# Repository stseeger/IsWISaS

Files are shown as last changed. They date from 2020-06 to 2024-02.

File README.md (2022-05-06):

# IsWISaS
(I)n-(s)itu (W)ater (I)sotope (Sa)mpling (S)ystem

This repository contains Hardware (circuit board designs), the respective Firmware and Software (a collection of scripts) that enable the user to control a set of electric solenoid valves and up to two mass flow controllers.

In conjunction with some in-situ gas sampling probes and a cavity ring down spectrometer (CRDS), this should facilitate fully automated long term in-situ measurements of stable water isotopes.

In case you need something that works, please contact me under: stefan.seeger@hydrology.uni-freiburg.de
There are working setups, but the Hardware is completely undocumented (most of my time is spent on getting results, not writing documentations) and the Software is constantly changing.

Right now everything in this repository is still work in progress. A technical note is planned...

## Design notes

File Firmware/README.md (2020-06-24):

Each of the different controller types should respond to the same set of serial text commands:  
  
**?**: return device class, devce type and version (seperated by spaces)  
**valve**: return the active valve  
**valve #**: activate valve # and close previous active valve  
**flow**: return the analog voltages (in mV) returned by the two mass flow controllers (seperated by spaces)  
**flow a b**: change the set point voltages of the two flow controllers (A and B) to a and b (in mV)

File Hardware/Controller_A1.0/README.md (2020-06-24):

This circuit board is meant to control up to two mass flow controllers and up to 16 solenoid valves.  
  
Part list:  
1 x Arduino Nano v3  
2 x ULN2803  
2 x 1kOhm Resitor  
2 x 100kOhm Resistor  
2 x 100µF Capacitator  
2 x PS/2 Port  
2 x 10 slot female header

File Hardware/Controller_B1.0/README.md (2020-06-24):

The main circuit board is meant to control up to two mass flow controllers and up to 8 solenoid valves.

Each extension circuit board can control up to 8 additional solenoid valves. The main board has one RJ-45 port that can be used to connect to the first extension and each extension has two RJ-45 ports (in and out), so that multiple extensions can be chained together.

The main board has a RJ-45 port which can be used to connect to an extension board which itself can control up to 8 solenoid valves.
  
Part list (main circuit board):  
1 x Arduino Nano v3  
1 x ULN2803  
2 x 1kOhm Resitor  
2 x 100kOhm Resistor  
2 x 100µF Capacitator  
2 x PS/2 Port  
1 x 8 slot female header  
1 x RJ-45 Port  
  
Part list (extension board):  
1 x 74HC595  
1 x ULN2803  
1 x 8 slot female header  
2 x RJ-45 Port

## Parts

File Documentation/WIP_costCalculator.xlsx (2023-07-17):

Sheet: fullSetup
# of setups | 1
# of WIPs | 76 | average tubing length [m] | 3
# of boxes | 10
part | EUR/piece | 1/WIP_or_setup | cost/WIP_or_setup | total amount | total cost | part # | url
MFC | 1207 | 2 | 2414 | 2 | 2414 | 35362L | https://analyt-mtc.de/de/contact-2
valve | 30 | 3 | 90 | 228 | 6840 | E210C-2W012 | https://shop.clippard.eu/en/product=e210c-2w012&id=evmmnc343t
valve block | 65.5 | 0.375 | 24.5625 | 28.5 | 1866.75 |  | http://www.schneider-fertigungstechnik.de/
mixing chamber | 21.36 | 1 | 21.36 | 76 | 1623.36 |  | https://kunststoffverarbeitung-freiburg.de/
probe head | 28.6 | 1 | 28.6 | 76 | 2173.6 |  | https://www.porex.com/
1/16" fitting bla | 3.93 | 1 | 3.93 | 76 | 298.68 | UP XP-201X | https://techlab.de/web/index.php?WSparam=2&WSdaten=5842@0
1/16" fitting red | 3.93 | 1 | 3.93 | 76 | 298.68 | UP XP-202X | https://techlab.de/web/index.php?WSparam=2&WSdaten=5844@0
1/16" nut blue | 2.26 | 1 | 2.26 | 76 | 171.76 | UP P-206 | https://techlab.de/web/index.php?WSparam=2&WSdaten=1989@0
ferrule | 2.16 | 1 | 2.16 | 76 | 164.16 | UP P-200X | https://techlab.de/web/index.php?WSparam=2&WSdaten=1978@0
1/8" fitting bla | 3.93 |  |  | 60 | 235.8 | UP XP-301X | https://techlab.de/web/index.php?WSparam=2&WSdaten=5878@0
1/16" FEP | 2.86 | 9 | 25.74 | 684 | 1956.24 | KAP 100.968 | https://techlab.de/web/index.php?WSparam=2&WSdaten=4537@0
9 mm PVC | 0.45 | 3 | 1.35 | 228 | 102.6 | PVC 69 | https://www.landefeld.de/artikel/de/pvc-schlauch-6x9mm-transparent-meterware/PVC%2069
 |  |  |  |  | 18145.63

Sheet: WIP
Setup characteristics
distance probe to valve manifold [m]: | 3 |  | Legend:
distance manifold to analyzer [m]: | 38.9 |  | fix input
probes per valve manifold: | 9.3 |  | variable input
number of lines per probe: | 3 |  | computed values
total number of probes: | 76
IsWIP cost calculation
Part | per probe | cost per piece [EUR] | cost per probe [EUR] | total cost [EUR] | pieces in stock | credit [EUR] | missing pieces | remaining cost [EUR]
mixing chamber | 1 | 15 | 17.85 | 1140.00 | 150 | 1140.00 | 0 | 0.00
probe head | 1 | 34 | 34.00 | 2584.00 | 150 | 2584.00 | 0 | 0.00
Flangeless nut+ferrule | 3 | 3.81 | 11.43 | 868.68 | 30 | 114.30 | 198 | 754.38
Aluminium pipe (10x3mm) | 0.1 | 10.4 | 1.04 | 79.04 | 1 | 10.40 | 7 | 72.80
PAFL-tubing (12x9mm) at shaft | 0.1 | 5.47 | 0.55 | 41.57 | 0 | 0.00 | 8 | 43.76
outer PVC-tubing (9x6mm) | 7.182795699 | 0.71 | 5.10 | 387.58 | 0 | 0.00 | 546 | 387.66
1/16” FEP-tubing | 9 | 2.86 | 25.74 | 1956.24 | 250 | 715.00 | 434 | 1241.24
1/8" FEP-tubing | 12.5483871 | 1.4 | 17.57 | 1335.15 | 0 | 0.00 | 954 | 1335.60
solenoid valve | 3 | 30 | 90.00 | 6840.00 | 48 | 1440.00 | 180 | 5400.00
valve manifold | 0.3225806452 | 65 | 20.97 | 1593.55 | 6 | 390.00 | 19 | 1235.00
complete probe |  |  | 224.24 | 16825.81 |  | 6393.70 |  | 10470.44

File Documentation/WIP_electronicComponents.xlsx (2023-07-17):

 |  | Controller C1.2 | Extension C1.2 | 8x3valveModule
 |  | 2 | 10 | 10
part | EUR/piece | 1/Controller | 1/Extension | 1/valveModule | totalAmount | total Cost | part# | url
Controller PCB | 6 | 1 | 0 | 0 | 2 | 12
Extension PCB | 2.3 | 0 | 1 | 0 | 10 | 23
valveModule PCB | 1.5 | 0 | 0 | 1 | 10 | 15
Arduino Nano | 18 | 1 | 0 | 0 | 2 | 36 |  | http://store.arduino.cc/products/arduino-nano
Arduino ProMini | 9 | 0 | 1 | 0 | 10 | 90 |  | https://www.sparkfun.com/products/11113
RS-485 Module | 2.9 | 1 | 1 | 0 | 12 | 34.8 |  | https://www.makershop.de/module/kommunikation-module/ttl-rs-485/
LM2596 HW411 | 1.5 | 1 | 0 | 0 | 2 | 3 |  | https://www.amazon.com/LM2596-Converter-Module-Supply-1-23V-30V/dp/B008BHBEE0
ULN2803 | 0.45 | 1 | 1 | 0 | 12 | 5.4 | ULN 2803A | https://www.reichelt.de/de/de/eight-darlington-arrays-dil-18-uln-2803a-p22085.html?search=uln2803&r=1
IC-Socket 18Pins | 0.07 | 1 | 1 | 0 | 12 | 0.84 | GS 18 | https://www.reichelt.de/ic-sockel-18-polig-doppelter-federkontakt-gs-18-p8210.html?search=GS+18
L78M05CV STM | 0.35 | 0 | 1 | 0 | 10 | 3.5 | L78M05CV STM | https://www.reichelt.de/de/en/voltage-regulator-fixed-5-v-0-5a-4-to-220-l78m05cv-stm-p216704.html?trstct=pos_7&nbc=1
L7812ACV STM | 0.35 | 0 | 1 | 0 | 10 | 3.5 | L7812ACV STM | https://www.reichelt.de/de/en/voltage-regulator-fixed-12-v-1-5a-2-to-220-l7812acv-stm-p216568.html?trstct=pos_2&nbc=1
RJ45 Socket | 0.4 | 1 | 2 | 0 | 22 | 8.8 | MEBP 8-8S | https://www.reichelt.de/de/en/modular-panel-jack-8-8-black-mebp-8-8s-p11372.html?&trstct=pos_4&nbc=1
miniDIN6 Socket | 0.94 | 1 | 0 | 0 | 2 | 1.88 | EB-DIOS M06G | https://www.reichelt.de/de/en/6-pin-mini-din-socket-green-shielded-eb-dios-m06g-p52028.html?search=mini+din+6&r=1
miniDIN6 Socket | 1.15 | 1 | 0 | 0 | 2 | 2.3 | EB-DIOS M06V | https://www.reichelt.de/de/en/6-pin-mini-din-socket-purple-shielded-eb-dios-m06v-p52029.html?nbc=1&trstct=lsbght_sldr::52028
DC-Socket 2.1mm | 1.2 | 1 | 0 | 0 | 2 | 2.4 | DC BU21 90 | https://www.reichelt.de/de/en/dc-socket-flat-contacts-2-1mm-90--dc-bu21-90-p183502.html?trstct=pos_12&nbc=1
DIP_Switch 4 | 0.24 | 0 | 1 | 0 | 10 | 2.4 | NT 04 | https://www.reichelt.de/dip-schalter-liegend-4-polig-nt-04-p13532.html?search=NT+04
R 430Ω | 0.08 | 0 | 0 | 1 | 10 | 0.8 | METALL 430 | https://www.reichelt.de/de/en/metal-film-resistor-430-ohm-metall-430-p11806.html?&trstct=pos_0&nbc=1
R 3.3kΩ | 0.04 | 2 | 1 | 0 | 14 | 0.56 | VI MBB02070C3301 | https://www.reichelt.de/de/en/thin-film-resistor-axial-0-6-w-3-3-kohm-1--vi-mbb02070c3301-p233725.html?trstct=pol_0&nbc=1
R 6.8kΩ | 0.04 | 0 | 1 | 0 | 10 | 0.4 | VI MBB02070C6801 | https://www.reichelt.de/de/en/thin-film-resistor-axial-0-6-w-6-8-kohm-1--vi-mbb02070c6801-p233765.html?trstct=pos_0&nbc=1
R 15kΩ | 0.04 | 0 | 1 | 0 | 10 | 0.4 | VI MBB02070C1502 | https://www.reichelt.de/de/en/thin-film-resistor-axial-0-6-w-15-kohm-1--vi-mbb02070c1502-p233688.html?trstct=pos_0&nbc=1
R 33kΩ | 0.04 | 0 | 1 | 0 | 10 | 0.4 | VI MBB02070C3302 | https://www.reichelt.de/de/en/thin-film-resistor-axial-0-6-w-33-kohm-1--vi-mbb02070c3302-p233726.html?trstct=pos_0&nbc=1
R 68kΩ | 0.04 | 0 | 1 | 0 | 10 | 0.4 | VI MBB02070C6802 | https://www.reichelt.de/de/en/thin-film-resistor-axial-0-6-w-68-kohm-1--vi-mbb02070c6802-p233766.html?trstct=pos_1&nbc=1
R 100kΩ | 0.04 | 2 | 0 | 0 | 4 | 0.16 | VI MBB02070C1003 | https://www.reichelt.de/de/en/thin-film-resistor-axial-0-6-w-100-kohm-1--vi-mbb02070c1003-p233667.html?trstct=pol_0&nbc=1
C 100μF (35V) | 0.05 | 0 | 1 | 0 | 10 | 0.5 | RAD 105 100/35 | https://www.reichelt.de/de/en/electrolytic-capacitor-105-c-spacing-2-5-mm-rad-105-100-35-p42401.html?trstct=pol_1&nbc=1
C 100μF (6.3V) | 1.6 | 2 | 0 | 0 | 4 | 6.4 | AVX TAP107M006SC | https://www.reichelt.de/de/en/tantalum-capacitor-100-f-6-3-v-avx-tap107m006sc-p246454.html?trstct=pos_7&nbc=1
C 100nF | 0.11 | 0 | 2 | 0 | 20 | 2.2 | C3X7R 100NA50 | https://www.reichelt.de/de/en/multi-layer-ceramic-capacitor-100nf-50v-125-c-c3x7r-100na50-p206877.html?trstct=pos_11&nbc=1
32 Pin Female | 1.99 | 1 | 0 | 0 | 2 | 3.98 | BKL 10120976 | https://www.reichelt.de/buchsenleiste-2-54mm-1x32-gerade-bkl-10120976-p266700.html?trstct=pol_0&nbc=1
12 Pin Female | 0.93 | 0 | 2 | 0 | 20 | 18.6 | BKL 10120951 | https://www.reichelt.de/buchsenleiste-2-54mm-1x12-gerade-bkl-10120951-p266676.html?trstct=pol_2&nbc=1
2x10 Pin Female | 0.35 | 1 | 1 | 0 | 12 | 4.2 | BL 2X10W 2,54 | https://www.reichelt.de/2x10pol-buchsenleiste-gewinkelt-rm-2-54-bl-2x10w-2-54-p6075.html?trstct=pol_2&nbc=1
2x10 Pin Male | 0.19 | 0 | 0 | 1 | 10 | 1.9 | SL 2X10W 2,54 | https://www.reichelt.de/2x10pol-stiftleiste-gewinkelt-rm-2-54-sl-2x10w-2-54-p19489.html?trstct=pos_0&nbc=1
4 Pin Female | 0.17 | 2 | 2 | 0 | 24 | 4.08 | MPE 094-1-004 | https://www.reichelt.de/buchsenleisten-2-54-mm-1x04-gerade-mpe-094-1-004-p119913.html?trstct=pol_3&nbc=1
2x3Pin Female | 0.31 | 0 | 0 | 8 | 80 | 24.8 | MPE 094-2-006 | https://www.reichelt.de/buchsenleisten-2-54-mm-2x03-gerade-mpe-094-2-006-p119927.html?trstct=pol_5&nbc=1
LED 3mm, green | 0.14 | 0 | 0 | 8 | 80 | 11.2 | LED 3MM 2MA GN | https://www.reichelt.de/led-3-mm-bedrahtet-gruen-3-2-mcd-60--led-3mm-2ma-gn-p21624.html?trstct=pos_1&nbc=1
 |  |  |  |  |  | 325.8

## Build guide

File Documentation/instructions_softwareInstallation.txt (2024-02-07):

Step 1:
In order to enable your computer to communicate with the Arduino Nano on the main controll board, you need to install the CH34x Serial driver.
Just enter "CH34x Serial driver" into your search engine of choice and select a trustworthy source.
here is one example of a source that works right now (2024-02-07):
https://sparks.gogo.co.nz/assets/_site_/downloads/CH34x_Install_Windows_v3_4.zip
or here (a link to my personal Dropbox, might not work for all eternity):
https://www.dropbox.com/s/80woki2fxfcg81h/CH34x_Install_Windows_v3_4.EXE

-------------------------
Step 1.5 (optional but recommended):

In case you just want to run the GUI, you can skip this step, but is recommended if you want to test the functionallity of the hardware independently from the GUI.

Install Arduino IDE :
https://www.arduino.cc/en/software
Via the Serial Monitor of the Arduino IDE you can directly send commands to the Arduino Nano on the IsWISaS main controller board.
Connect main controller Arduino to Computer, chose the correct COM-Port and select a Baud-rate of 9600.
The main controller recognizes three commands "?", "valve" and "flow":

? 
identify: The controller should return its name and version

valve
If called without arguments, the controller should return the currently opened valves.

valve <box>#<valve> [<secondaryBox>#<valve>]
open one or two specific valves at once.
<box> 0 is the main controller, higher numbers (1-15) refer to extensions whose IDs are determined by the red dip switches on the extension boards
<valve> refers to a valve on the respective box
[<secondaryBox>#<valve>] (without the square brackets) is optional and can be used to open a secondary valve. In a simple setup, this option is not used.

flow
If called without arguments, the controller should return the current flow rates (possible range mapped to values between 0 and 255) of the two flow controllers

flow <flowRateA> <flowRateB>
If two numbers (possible ranges mapped between 0 and 255) are passed, they will be used to set the flow rate targets of the two flow controllers.

-------------------------
Step 2:
Install Python 3:
https://www.python.org/downloads/

-------------------------
Step 3:
Install the pySerial module :
press: windows-key + R
enter: cmd
enter: <python> -m pip install pyserial
(<python> should contain the path to the python3 installation, default on the picarro might be the path to python2)

-------------------------
Step 4:
Extract the IsWISaS/Software directory to your Picarro's Desktop
Remove "Desktop>\IsWISaS\Software\temp\serial.cch"
("serial.cch" is meant to remember the Com-Port to which the Arduino is connected. This will be constant once your setup is ready, but It is impossible to tell in advance what the Com-Port will be.
 Without "serial.cch" all available Com-Ports are scanned automatically and the right one will be identified and saved into a new serial.cch and loaded without scanning all available Ports upon subsequent starts of the IsWISaS-GUI)

-------------------------
Step 5:
create a link to the IsWISaS_GUI:
  right click on your desktop -> New -> shortcut
Target:   <path to your python3 executable> GUI_IsWISaS.py
Start in: <path to your Desktop>\IsWISaS\Software\scripts

Step 6:
Now you can adapt the Desktop/IsWISaS/Software/config/valve.cfg to match your setup.

Step 7:
Connect the Arduino Nano of the IsWISaS main controller board to your Computer (using a Mini-USB cable).
Start IsWISaS-GUI by clicking on the shortcut that was created in step 5.

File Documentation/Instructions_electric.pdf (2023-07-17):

## Controller board

- Connect to Picarro (with the included Mini-USB
cable)

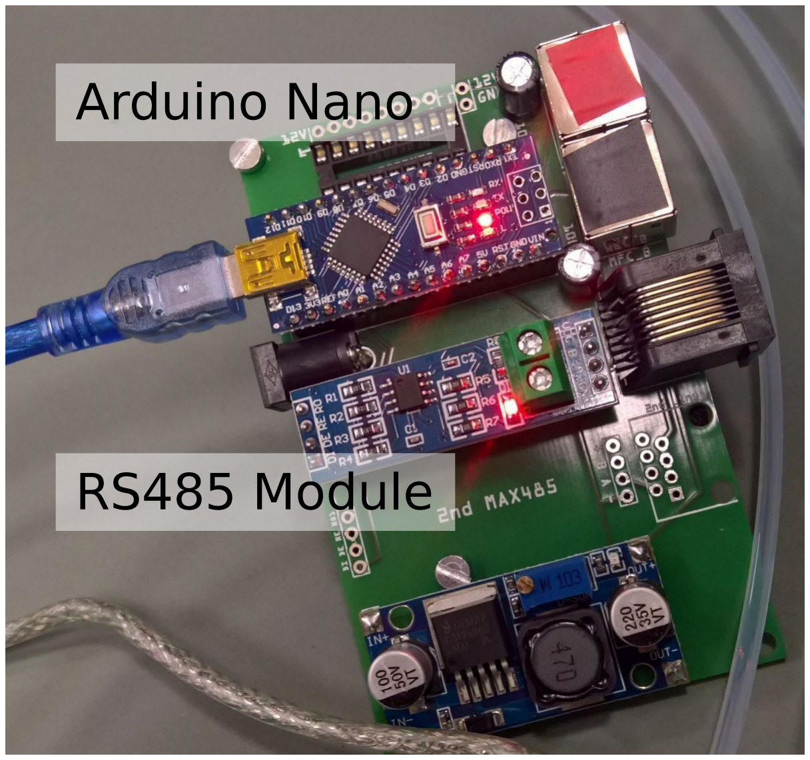
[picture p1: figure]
Arduino Nano; RS485 Module

- Red LEDs at Arduino
and RS485 Module

### should be lit

## Mass flow controllers (MFCs)

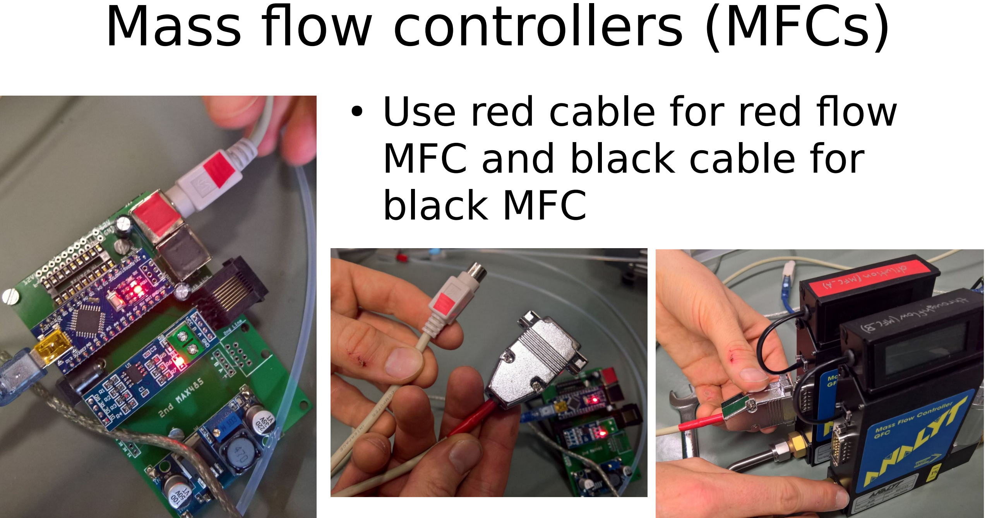
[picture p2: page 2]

- Use red cable for red flow MFC and black cable for

### black MFC

## Controller → Plotbox

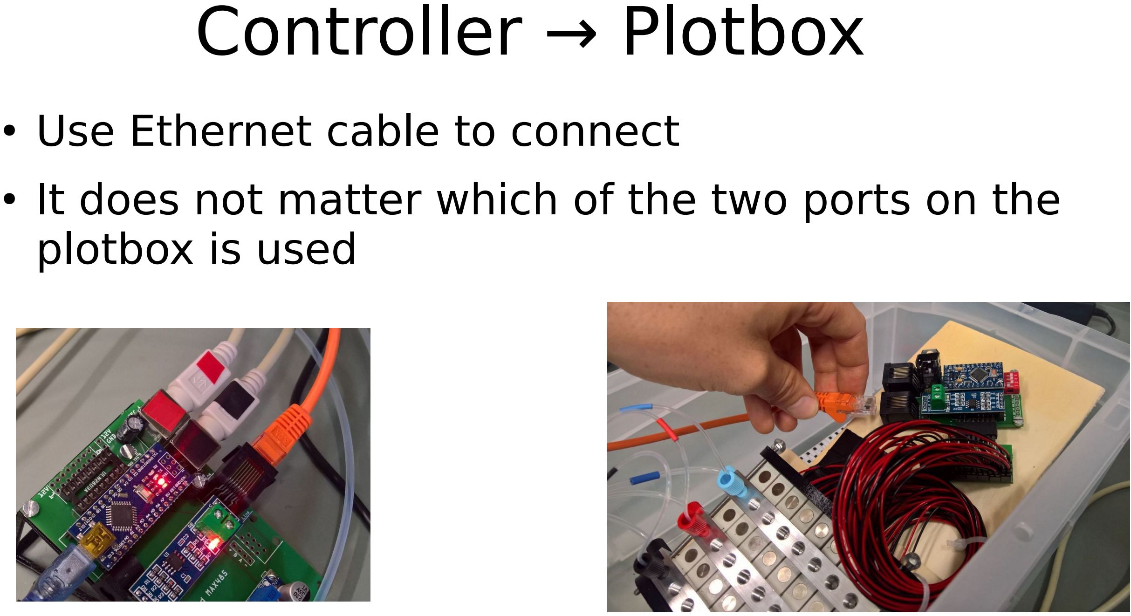
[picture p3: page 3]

- Use Ethernet cable to connect
- It does not matter which of the two ports on the plotbox is used

## Plotbox → Plotbox

- Connect to the next plotbox with another Ethernet cable

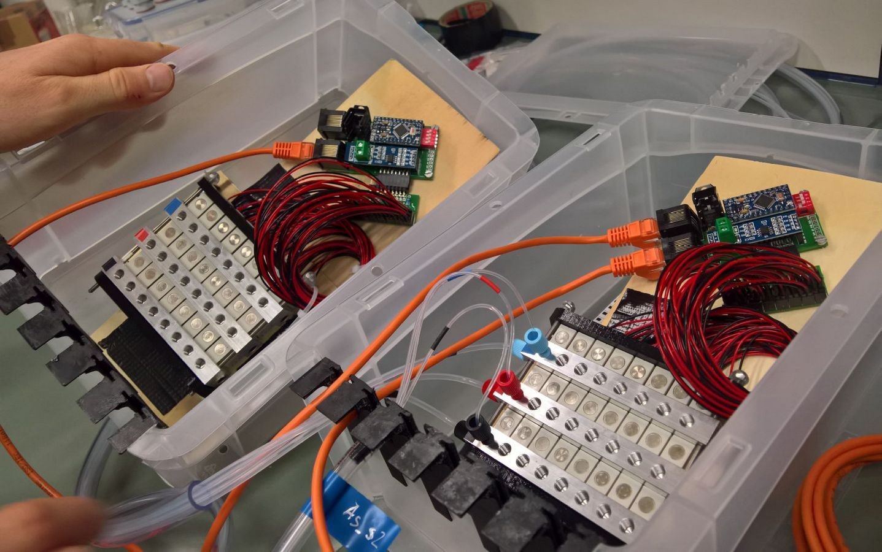
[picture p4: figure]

- address of plotbox is determined by DIP-switch (right finger)

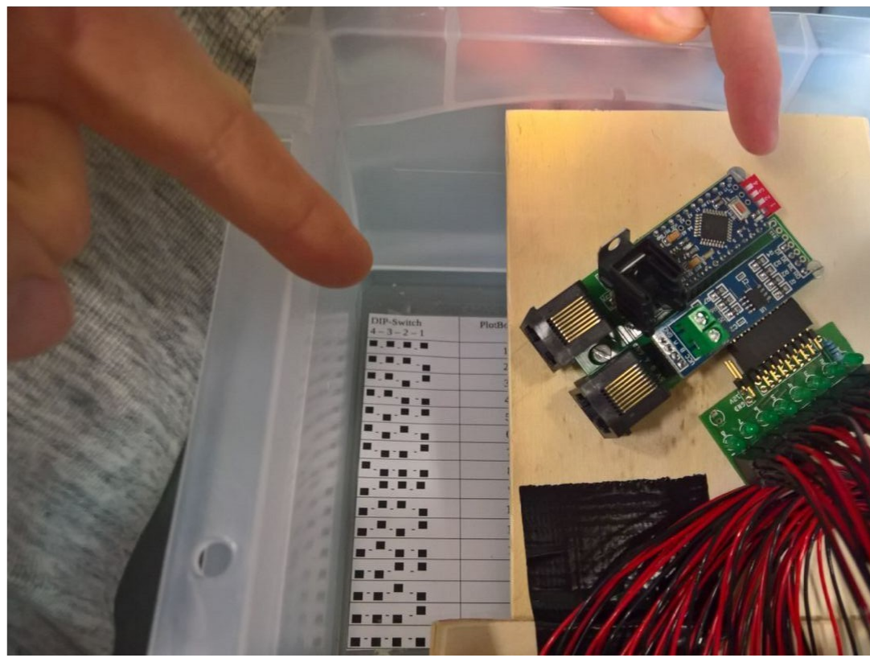
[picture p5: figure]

- each plotbox contains lookup table (left finger) listing addresses resulting from switch positions
- if all four switches are down, the controller goes into demo mode (cycling through all valves in rapid succession)

## Set plotbox address

## Power supply

- Plug included power
supply into controller
board

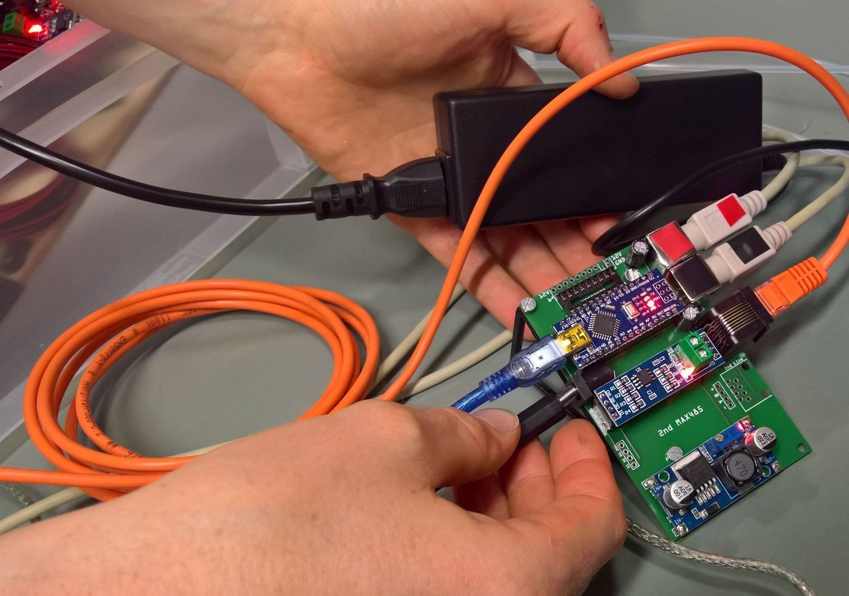
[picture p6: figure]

→ this powers up the
flow controllers and the
connected plot boxes
- Input voltages between
16 and 24 Volts should
be fine

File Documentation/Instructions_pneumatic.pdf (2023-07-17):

## Gas supply

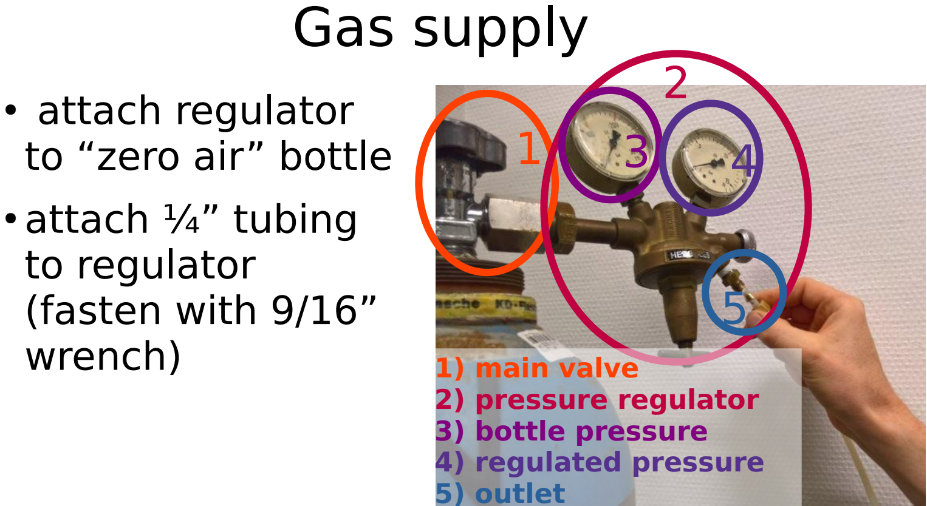
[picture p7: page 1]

- attach regulator
to “zero air” bottle
- attach ¼” tubing
to regulator
(fasten with 9/16”
wrench)

1

2
3 4

5

1) main valve
2) pressure regulator
3) bottle pressure
4) regulated pressure
5) outlet

## Gas supply

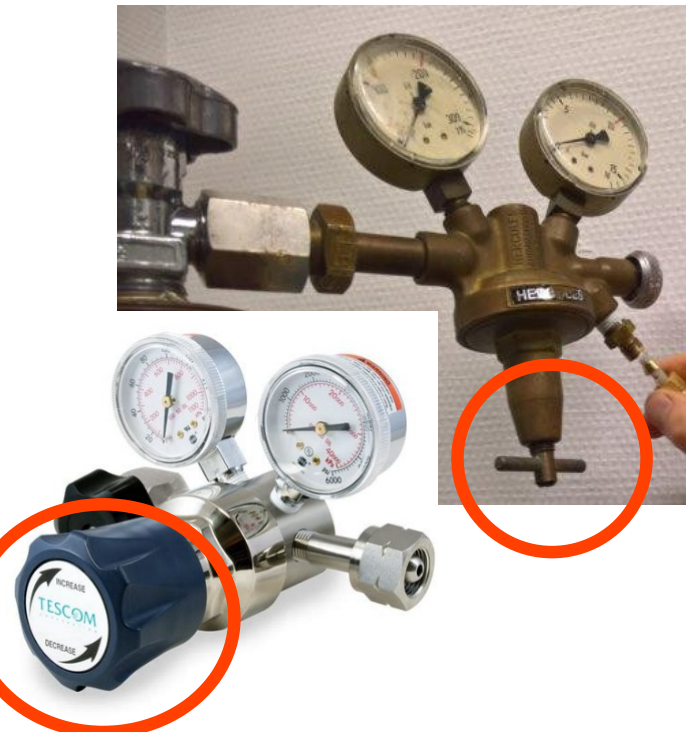
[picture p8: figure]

- The valve to regulate
the pressure at the
outlet might look
different at different
regulators

## Gas supply

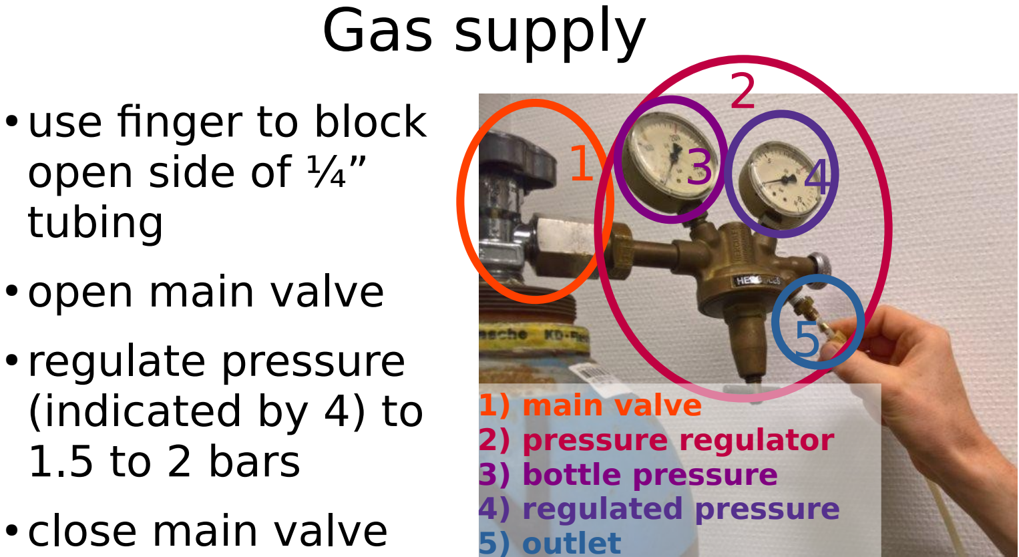
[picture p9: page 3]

- use finger to block
open side of ¼”
tubing
- open main valve
- regulate pressure
(indicated by 4) to
1.5 to 2 bars
- close main valve

1

2
3 4

5

1) main valve
2) pressure regulator
3) bottle pressure
4) regulated pressure
5) outlet

## Mass flow controller inlets

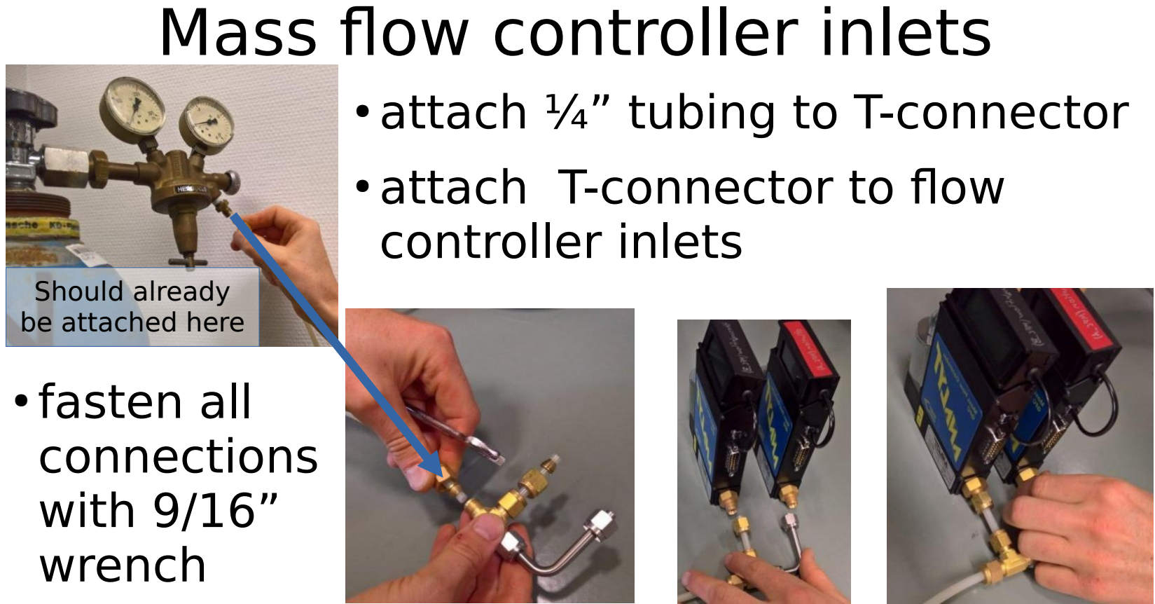
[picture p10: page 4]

- attach ¼” tubing to T-connector
- attach T-connector to flow controller inlets
- fasten all
connections
with 9/16”
wrench

Should already
be attached here

## Mass flow controller outlets

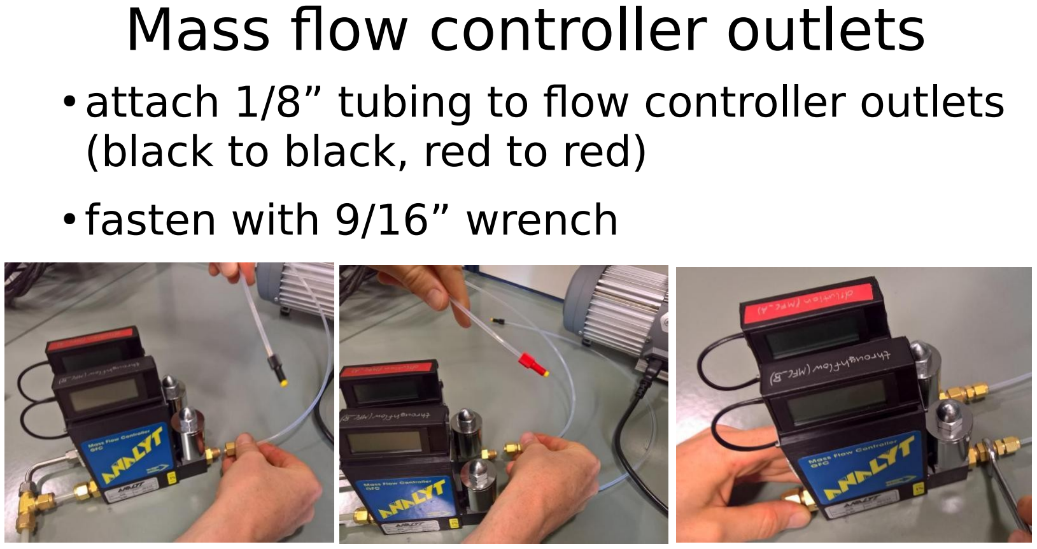
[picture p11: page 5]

- attach 1/8” tubing to flow controller outlets (black to black, red to red)
- fasten with 9/16” wrench

## Picarro inlet

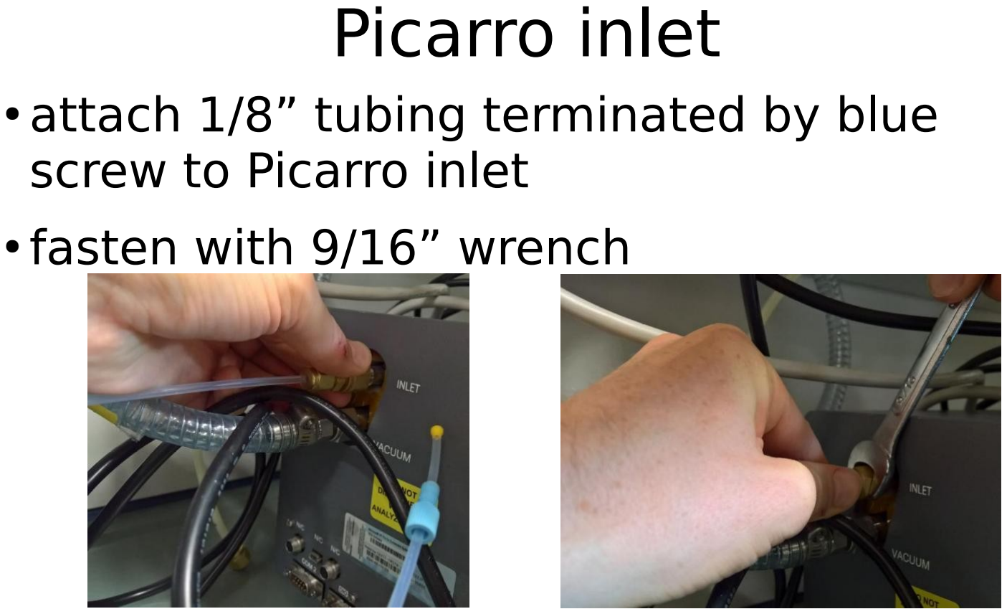
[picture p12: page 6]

- attach 1/8” tubing terminated by blue screw to Picarro inlet
- fasten with 9/16” wrench

## Plotbox manifolds

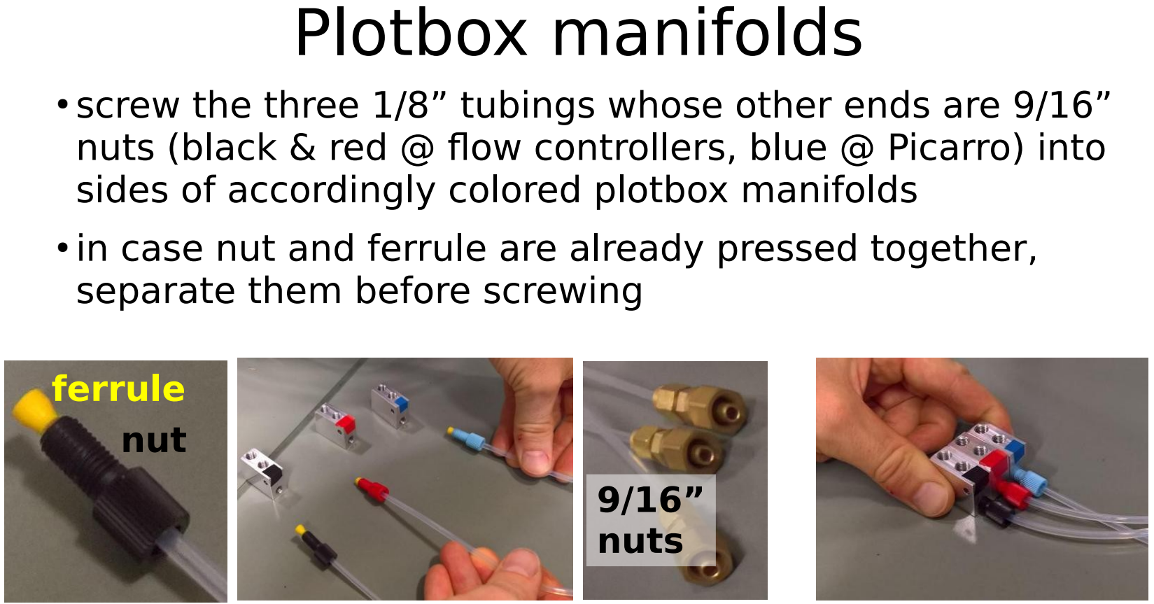
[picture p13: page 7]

- screw the three 1/8” tubings whose other ends are 9/16” nuts (black & red @ flow controllers, blue @ Picarro) into sides of accordingly colored plotbox manifolds
- in case nut and ferrule are already pressed together, separate them before screwing

nut

ferrule

9/16”
nuts

## Plotboxes

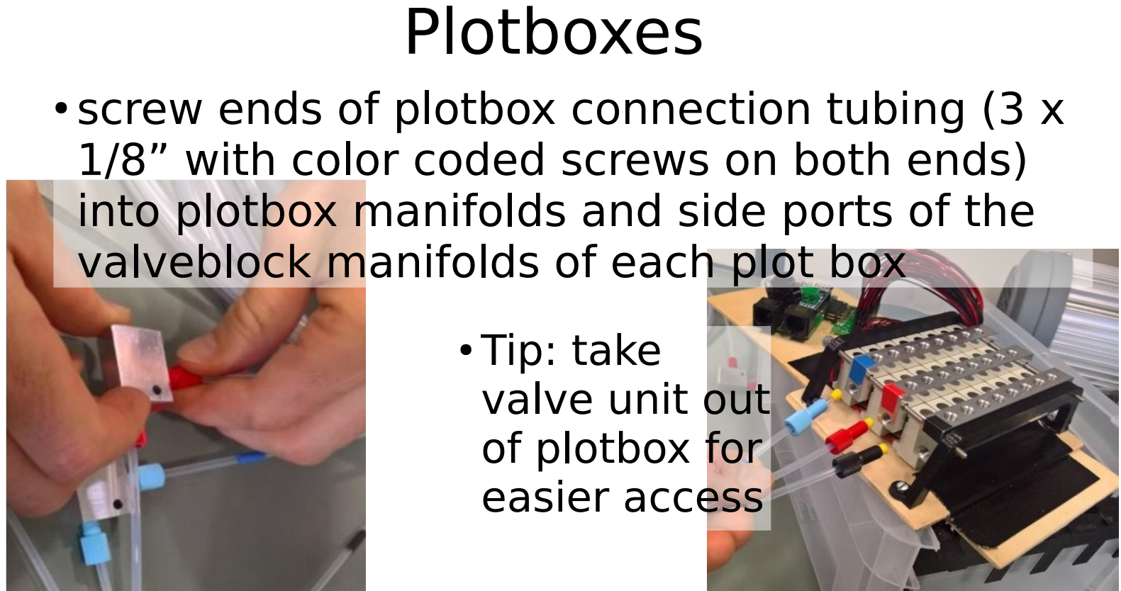
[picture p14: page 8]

- screw ends of plotbox connection tubing (3 x 1/8” with color coded screws on both ends) into plotbox manifolds and side ports of the valveblock manifolds of each plot box
- Tip: take
valve unit out
of plotbox for
easier access

## Plotboxes

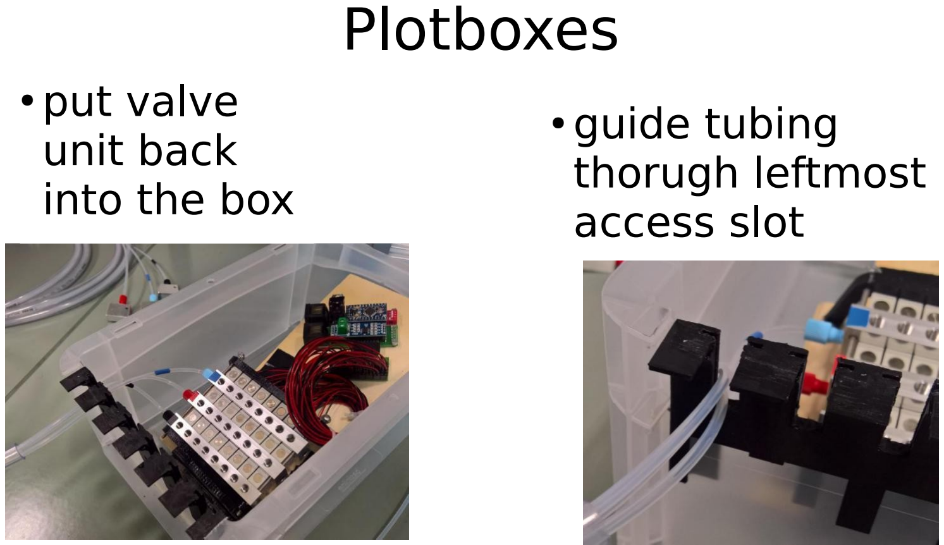
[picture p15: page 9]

- put valve
unit back
into the box
- guide tubing
thorugh leftmost
access slot

## Probes

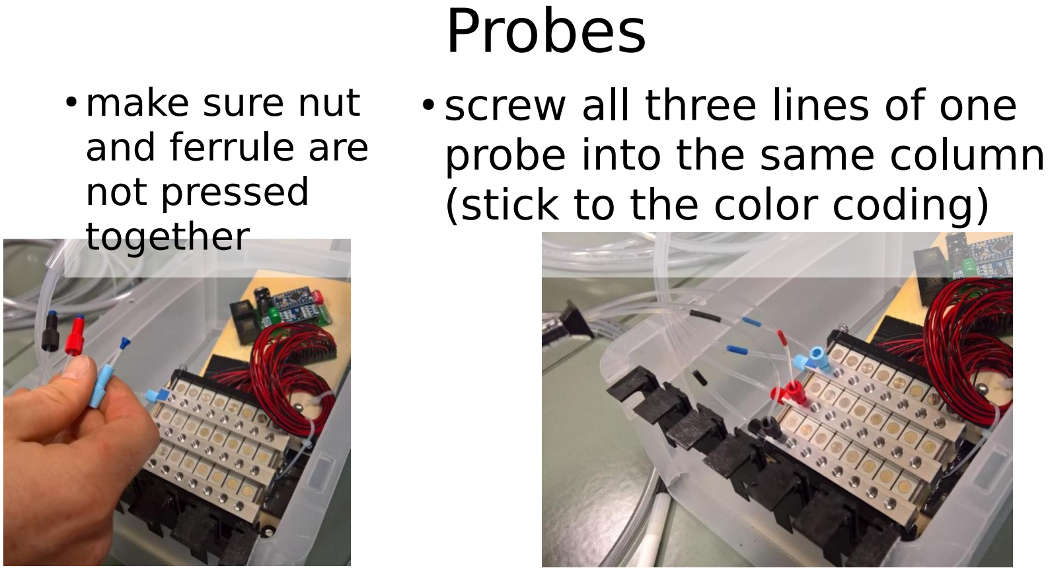
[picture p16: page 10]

- make sure nut
and ferrule are
not pressed
together
- screw all three lines of one probe into the same column (stick to the color coding)

## Probes

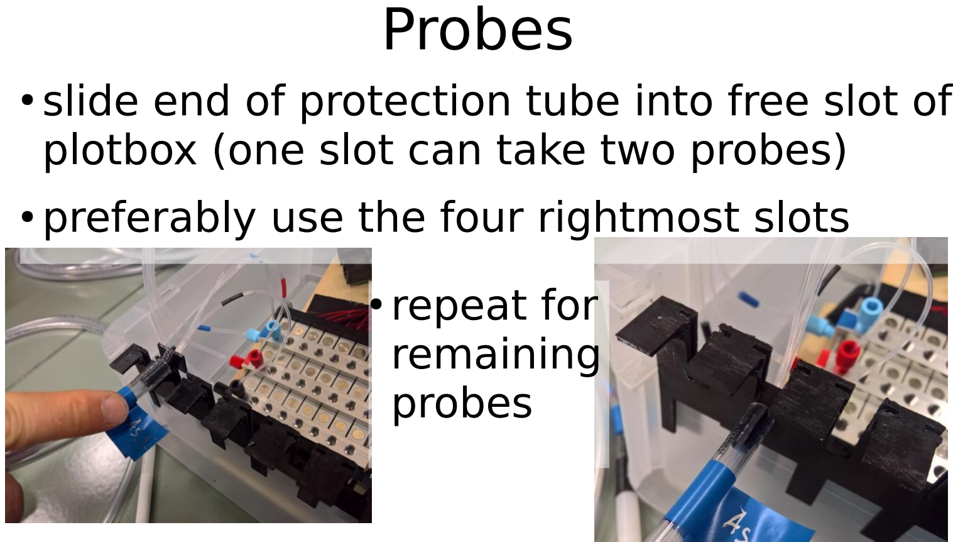
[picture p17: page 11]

- slide end of protection tube into free slot of plotbox (one slot can take two probes)
- preferably use the four rightmost slots
- repeat for
remaining
probes

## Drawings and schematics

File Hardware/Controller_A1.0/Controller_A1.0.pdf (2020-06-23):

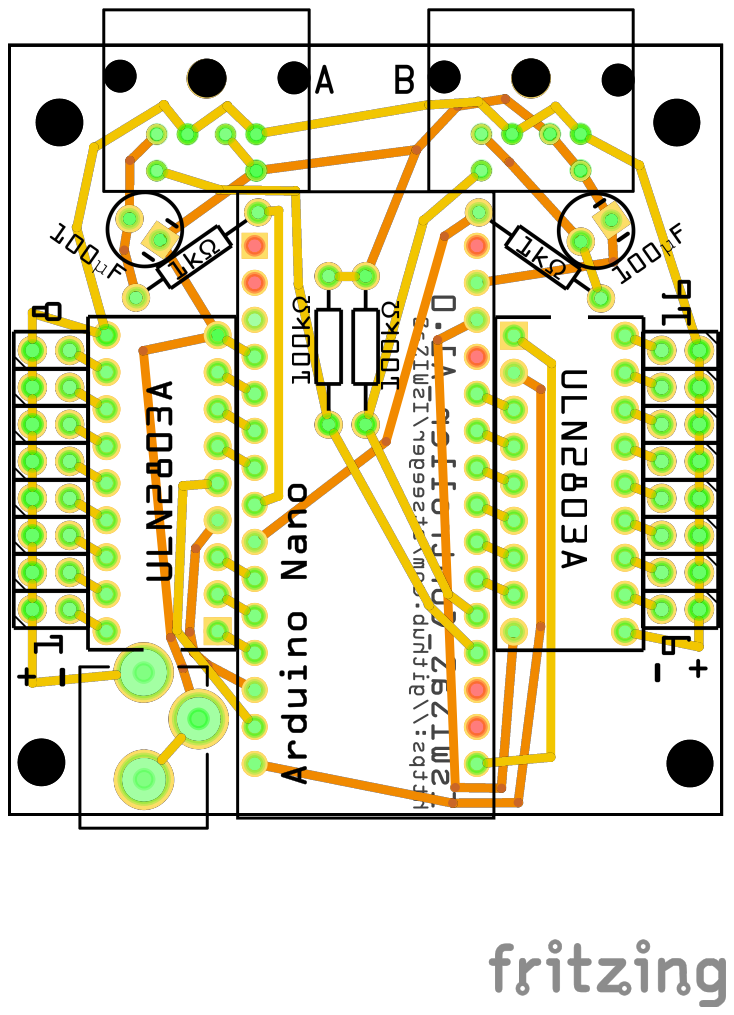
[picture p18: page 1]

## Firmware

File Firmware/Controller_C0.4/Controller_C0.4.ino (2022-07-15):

#include "src/CmdArduino//Cmd.h"
#include <SoftwareSerial.h>

#define DEVICE "IsWISaS_Controller"
#define MODEL "C"
#define VERSION "0.4"

#define INPUT_BUFFER_SIZE 32
char inputBuffer[INPUT_BUFFER_SIZE];
char boxBuffer[3];
char slotBuffer[3];
char checksumBuffer[3];

/*-----( Declare Constants and Pin Numbers )-----*/
#define portOne_RX 12  //Serial Receive pin
#define portOne_TX A0  //Serial Transmit pin
#define portOne_EN 13  //RS485 Direction control

#define portTwo_RX A4  //Serial Receive pin
#define portTwo_TX A3  //Serial Transmit pin
#define portTwo_EN A2  //RS485 Direction control

#define RS485Transmit    HIGH
#define RS485Receive     LOW
#define RS485_BAUDRATE 1200
/*-----( Declare objects )-----*/
SoftwareSerial portOne(portOne_RX, portOne_TX);
SoftwareSerial portTwo(portTwo_RX, portTwo_TX);
/*-----------------------------------------*/
struct valveSlotType{
  byte box;
  byte slot;  
};

//----------------------------------------



//------- valve control stuff ----------------
#define VALVE_COUNT 8
int valvePins[VALVE_COUNT] = {9, 8, 7, 10, 11, 4, 3, 2};

valveSlotType primaryValve   = {1,1};
valveSlotType groupValve     = {0,0};

//.........................................
valveSlotType parse_valveSlot(char *arg){
  valveSlotType valveSlot;
  byte value;
  char *pch;
  pch = strtok(arg,"#");
  for(byte i=0; i<2; i++){
    if(pch == NULL) break;
    value =  atoi(pch);
    
    if(i==0){
      valveSlot.slot = value;
      valveSlot.box = 0;
    }else{
      valveSlot.box = valveSlot.slot;
      valveSlot.slot = value;
    }   
    pch = strtok(NULL, "#");
  }
  return valveSlot;
}

//.........................................
void update_valves(){
  for(byte i=0; i < VALVE_COUNT; i++){
        digitalWrite(valvePins[i], ((primaryValve.box==0)   & (i == primaryValve.slot-1))|                                   
                                   ((groupValve.box==0)     & (i == groupValve.slot-1)));
  }  

  
  SoftwareSerial SWSPort[2] = {portOne, portTwo};
  int SWS_EN_PIN[2] = {portOne_EN, portTwo_EN};
  
  for(byte n=0; n<2; n++){
    digitalWrite(SWS_EN_PIN[n],HIGH);
    delay(50);
    SWSPort[n].print("valve ");
    SWSPort[n].print(primaryValve.box);
    SWSPort[n].print('#');
    SWSPort[n].print(primaryValve.slot);
    SWSPort[n].print('#');
    SWSPort[n].print(groupValve.box);
    SWSPort[n].print('#');
    SWSPort[n].println(groupValve.slot);
    digitalWrite(SWS_EN_PIN[n],LOW);   
 } 
}

//.........................................
void get_activeValve(){  
  Serial.print("valve>");
  Serial.print(primaryValve.box);
  Serial.print('#');
  Serial.print(primaryValve.slot);  

  Serial.print(' ');
  Serial.print(groupValve.box);
  Serial.print('#');
  Serial.print(groupValve.slot);
  
  Serial.println();
}

//------- flow control stuff  ----------------
#define PWM_PIN_A 5
#define ANA_PIN_A A6

#define PWM_PIN_B 6
#define ANA_PIN_B A7

#define PERIOD 1e2
#define SAMPLES 100

float valueA = 0;
float valueB = 0;

void set_pwmPin(byte pin, int value){
  if(value < 0) value = 0;
  if(value >1023) value = 1023;
  analogWrite(pin, value);
}

//......................................
void measure_anaPins(){
  unsigned long sumA = 0;
  unsigned long sumB = 0;

  for(int i=0; i< SAMPLES; i++){
    sumA+=analogRead(ANA_PIN_A);
    sumB+=analogRead(ANA_PIN_B);
  }

  valueA = float(sumA)/float(SAMPLES)/4;
  valueB = float(sumB)/float(SAMPLES)/4;
  
}

void open_RS485(byte port){
  if(port==1){
    digitalWrite(portOne_EN,HIGH);    
  }
  if(port==2){
    digitalWrite(portTwo_EN,HIGH);
  }
  delay(50);
}

void close_RS485(byte port){
  if(port==1){
    digitalWrite(portOne_EN,LOW);    
  }
  if(port==2){
    digitalWrite(portTwo_EN,LOW);
  }
}

byte get_RS485Response(byte portNumber){
  byte responseLength=0;
  if(portNumber==1){      
      responseLength = portOne.readBytesUntil('\0',inputBuffer,INPUT_BUFFER_SIZE-1); 
  }
  if(portNumber==2){
    responseLength = portTwo.readBytesUntil('\0',inputBuffer,INPUT_BUFFER_SIZE-1);
  }

  if(responseLength){
    inputBuffer[responseLength-1]='\0';
    byte offset=0;
    for(byte i=0; i<responseLength;i++){
      if(inputBuffer[offset]=='<') break;
      offset++;
    }    
    Serial.println(inputBuffer+offset);
    inputBuffer[0]='\0';
  }else{
    Serial.println("< x");
  } 

   return responseLength;
}



//==========================================

void cmd_identify(int arg_cnt, char **args){

  byte targetID = 0;
  if(arg_cnt>1) targetID = atoi(args[1]);

  if(targetID){
    SoftwareSerial SWSPort[2] = {portOne, portTwo};
    byte responseLength = 0;
    for(byte i=0; i<2; i++){
      open_RS485(i+1);
        SWSPort[i].print("? ");
        SWSPort[i].println(targetID);
      close_RS485(i+1);
      delay(20);
      responseLength = get_RS485Response(i+1);
      if(responseLength) break;
    }
    return;
  }
  
  Serial.print(DEVICE);
  Serial.print(' ');
  Serial.print(MODEL);
  Serial.print(' ');
  Serial.println(VERSION);  
}

//......................................
void cmd_scan(int arg_cnt, char **args){
  
  byte boxID = 0;
  
  if(arg_cnt==2){
    boxID =  atoi(args[1]);
  }  

  if(boxID==0){    
    Serial.print(VALVE_COUNT);
    Serial.print(";");
    Serial.println(VALVE_COUNT);
    return;
  }  

  SoftwareSerial SWSPort[2] = {portOne, portTwo};
  byte responseLength = 0;
  for(byte i=0; i<2; i++){
    open_RS485(i+1);
    SWSPort[i].print("?? ");
    SWSPort[i].println(boxID);
    close_RS485(i+1);
    delay(20);
    responseLength = get_RS485Response(i+1);
    if(responseLength) break;
  }
}
//......................................
void cmd_valve(int arg_cnt, char **args){

  // in case no second argument was passed, just print the active valve
  if(arg_cnt < 2){
    get_activeValve();
    return;
  }
  primaryValve = parse_valveSlot(args[1]);
  
  if(arg_cnt > 2)
    groupValve = parse_valveSlot(args[2]);
  
  update_valves();  
}

//........................................
void cmd_test(int arg_cnt, char **args){
  
  if(arg_cnt > 1){
    byte targetID = atoi(args[1]);
    if(targetID){      
      SoftwareSerial SWSPort[2] = {portOne, portTwo};      
      for(byte i=0; i<2; i++){
        open_RS485(i+1);
          SWSPort[i].print("test ");
          SWSPort[i].println(targetID);
        close_RS485(i+1);
      }      
      return;
    } 
  }  
  
  valveSlotType backupPrimaryValve = {primaryValve.box, primaryValve.slot};
  primaryValve.box=16;

    for(byte n=0; n<VALVE_COUNT; n++){    
      primaryValve.slot=(n+1);
      update_valves();
      delay(500);
    }

   primaryValve.box = backupPrimaryValve.box;
   primaryValve.slot = backupPrimaryValve.slot;
}
//........................................

void cmd_flow(int arg_cnt, char **args){
  
  // in case no further argument were passed, just print the current analog voltages of the analog pins
  if(arg_cnt != 3){
    measure_anaPins();
    Serial.print("flow>");
    Serial.print(valueA);
    Serial.print("|");
    Serial.println(valueB);
    return;
  }
  
  // in case the second argument was 'A', interpret the third as target value for A
  if(args[1][0] == 'A'){
    set_pwmPin(PWM_PIN_A, atoi(args[2]));
    return;
  }

  // in case the second argument was 'B', interpret the third as target value for B
  if(args[1][0] == 'B'){
    set_pwmPin(PWM_PIN_B, atoi(args[2]));
    return;
  }

  // otherwise
  set_pwmPin(PWM_PIN_A, atoi(args[1]));
  set_pwmPin(PWM_PIN_B, atoi(args[2]));
}
//-----------------------------
void setup() {
  cmdInit(9600);  
  cmdAdd("?", cmd_identify);
  cmdAdd("??", cmd_scan);
  cmdAdd("test", cmd_test);
  cmdAdd("valve", cmd_valve);
  cmdAdd("flow", cmd_flow);  

  // Software Serial
  pinMode(portOne_EN, OUTPUT);
  pinMode(portTwo_EN, OUTPUT);
  portTwo.begin(RS485_BAUDRATE); // Start the software serial port
  portOne.begin(RS485_BAUDRATE); // Start the software serial port
  
  for(byte i = 0; i<VALVE_COUNT; i++){
    pinMode(valvePins[i], OUTPUT);
    digitalWrite(valvePins[i], LOW);
  }
  //pinMode(BOX0_FLUSH_VALVE, OUTPUT);
  //digitalWrite(BOX0_FLUSH_VALVE, LOW);
  
  update_valves();
  cmd_identify(0,NULL);
  Serial.print(">> ");
}

//------------------------------

void loop() {
  cmdPoll();
}

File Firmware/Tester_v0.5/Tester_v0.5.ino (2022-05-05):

#define LED_PIN_PATTERN 10
#define LED_PIN_ERROR 11
#define LED_PIN_UNITY 12

byte ledPins[3] = {LED_PIN_PATTERN, LED_PIN_UNITY, LED_PIN_ERROR};

byte anaPins[8] = {A0,A4,A1,A2,A3,A5,A6,A7};
byte digPins[8] = {2,6,3,4,5,7,8,9};

byte pattern[8][8] = {{1,0,0,0,0,0,0,0},
                      {0,1,0,0,0,0,0,0},
                      {0,0,1,1,1,0,0,0},
                      {0,0,1,1,1,0,0,0},
                      {0,0,1,1,1,0,0,0},
                      {0,0,0,0,0,1,1,1},
                      {0,0,0,0,0,1,1,1},
                      {0,0,0,0,0,1,1,1}};
void setup() {
  Serial.begin(9600);

  for(byte i=0;i<3;i++){    
    pinMode(ledPins[i], OUTPUT);
    digitalWrite(ledPins[i], LOW);
  }
  
  for(byte i=0;i<8;i++){
      pinMode(anaPins[i], INPUT_PULLUP);
      pinMode(digPins[i], INPUT);
      digitalWrite(digPins[i],HIGH);
  }
}

void loop() {

  boolean patternMatch = 1;
  boolean unityMatch = 1;
  boolean freeFloating = 1;
  boolean Error = 0;
  
  for(byte n=0;n<8;n++){
    pinMode(digPins[n],OUTPUT);
    digitalWrite(digPins[n],LOW);
    for(byte i=0;i<8;i++){
       //if(i>0) Serial.print(" ");
       int val = analogRead(anaPins[i]);
       bool isConnected = (1023-val)>990;
       patternMatch = patternMatch & pattern[n][i] == isConnected;
       unityMatch = unityMatch & (n==i)==isConnected;
       freeFloating = freeFloating & !isConnected;
       //Serial.print(isConnected);
       delay(5);
    }
    //Serial.println("");
    digitalWrite(digPins[n],HIGH);
    pinMode(digPins[n],INPUT);    
  }
  //Serial.println("----------------");
  if(patternMatch | unityMatch | freeFloating){
    //if(patternMatch) Serial.println("Pattern matched!");
    //if(unityMatch)   Serial.println("Unity matched!"); 
    //if(freeFloating) Serial.println("Floating free!");
    byte a=1;    
  }else{
    Error=1;
    //Serial.println("Something is wrong!");
  }
  //Serial.println("================");

  for(byte i=0;i<3;i++){    
    digitalWrite(ledPins[i], LOW);
  }

  if(patternMatch) digitalWrite(LED_PIN_PATTERN,HIGH);
  if(unityMatch) digitalWrite(LED_PIN_UNITY,HIGH);
  if(Error) digitalWrite(LED_PIN_ERROR,HIGH);
  
  delay(100);
}

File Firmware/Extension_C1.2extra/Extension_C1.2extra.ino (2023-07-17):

#include "src/CmdArduino//Cmd.h"
#include <EEPROM.h>

#define DEVICE "IsWISaS_Extension"
#define MODEL "C"
#define VERSION "1.2extra"

#define RS485_BAUDRATE 1200
#define RS485_MODE_CONTROL_PIN 13

#define INPUT_BUFFER_SIZE 32
char inputBuffer[INPUT_BUFFER_SIZE];

#define VALVE_COUNT 8
const int valvePins[VALVE_COUNT] = {2, 3, 4, 5, 6, 7, 8, 9};

#define DRAIN_VALVE_A 12
#define DRAIN_VALVE_B A0
#define DRAIN_SECONDS_ADDRESS 0
unsigned int drainSeconds;

#define ID_PIN A3
#define ANALOG_ID_TOLERANCE 7
#define ID_TABLE_SIZE 16
const int analogIdVals[ID_TABLE_SIZE] = {   0,  45,  90, 129, 182, 214, 245, 272,
                                          330, 352, 374, 393, 420, 436, 453, 468};
                                          
struct valveSlotType{
  byte box;
  int slot;  
};

unsigned long drainStart=0;
bool drainTriggerSet = false;

valveSlotType primaryValve   = {0,9};
valveSlotType secondaryValve = {0,0};

byte id = 0;

//--------------------------------------------
byte get_id(){
  int analogReading = analogRead(ID_PIN);
  for(byte i=0; i<ID_TABLE_SIZE; i++){
    if(analogReading >= (analogIdVals[i] - ANALOG_ID_TOLERANCE)&
       analogReading <= (analogIdVals[i] + ANALOG_ID_TOLERANCE)){
          return(i+1);          
       }
  }
  return(0);
}
//--------------------------------------------
void update_valves(){

   id = get_id();
  
  for(byte i=0; i < VALVE_COUNT; i++){
        digitalWrite(valvePins[i], ((primaryValve.box == id)   & (i == primaryValve.slot-1)) |
                                   ((secondaryValve.box == id) & (i == secondaryValve.slot-1)));
  }

  if((primaryValve.box==id & primaryValve.slot==VALVE_COUNT) |
     (secondaryValve.box==id & secondaryValve.slot==VALVE_COUNT)){
    drainTriggerSet=true;
  }
  
  if(drainTriggerSet & !((primaryValve.box==id | secondaryValve.box==id))){                         
    drainStart=millis();
    drainTriggerSet = false;
  }

  if(drainStart>0){
    unsigned long timeDiff = millis() - drainStart;
    digitalWrite(DRAIN_VALVE_A, timeDiff < drainSeconds*1000);
    digitalWrite(DRAIN_VALVE_B, (timeDiff > drainSeconds*1000) & (timeDiff < 2*drainSeconds*1000));
    if(timeDiff > 2*drainSeconds*1000) drainStart=0;
  }else{
    digitalWrite(DRAIN_VALVE_A, LOW);
    digitalWrite(DRAIN_VALVE_B, LOW);
  }
  
}
//--------------------------------------------
valveSlotType parse_valveSlot(char *arg){
  valveSlotType valveSlot;
  byte value;
  char *pch;
  pch = strtok(arg,"#");
  for(byte i=0; i<2; i++){
    if(pch == NULL) break;
    value =  atoi(pch);
    
    if(i==0){
      valveSlot.slot = value;
      valveSlot.box = 0;
    }else{
      valveSlot.box = valveSlot.slot;
      valveSlot.slot = value;
    }   
    pch = strtok(NULL, "#");
  }
  return valveSlot;
}
//--------------------------------------------
void cmd_valve(int arg_cnt, char **args){

  // in case no second argument was passed return
  if(arg_cnt < 2){    
    return;
  }
  primaryValve = parse_valveSlot(args[1]);

  if(arg_cnt >2)
    secondaryValve = parse_valveSlot(args[2]);

  //...change time to drain the valves and store change to EEPROM ...........
  if(primaryValve.box==255){
    drainSeconds = primaryValve.slot;
    EEPROM.put(DRAIN_SECONDS_ADDRESS, drainSeconds);    
  }
  //..........................
}
//--------------------------------------------
void cmd_identify(int arg_cnt, char **args){
  Serial.print(DEVICE);
  Serial.print(" ");
  Serial.print(MODEL);
  Serial.print(" ");
  Serial.println(VERSION);
}
//--------------------------------------------
void RS485Poll(){

  if(!Serial.available()) return;
  
  int n = Serial.readBytesUntil(13,inputBuffer,INPUT_BUFFER_SIZE-2);  
  inputBuffer[n] = '\n';
  inputBuffer[n+1] = '\0';

  if(inputBuffer[n] != '\n' | inputBuffer[0] == '\n') return;
  
  byte i=0;
  if(inputBuffer[0]!='\n') while(i<INPUT_BUFFER_SIZE){
    if(inputBuffer[i]=='\0') break;
    //Serial.print(inputBuffer[i]);
    i++;       
  }      
  cmd_parse(inputBuffer);
  while(Serial.available()){
    Serial.read();
  }
}
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

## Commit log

2020-06-24 Modifications to board designs for models B and C, some changes to the scripts
    [Controller_A1.0.fzz, Controller_B1.0.fzz, Controller_B1.0_doubleExtension.fzz, Controller_B1.0_master.fzz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]
2020-07-03 some updates...
    [Controller_B1.0.fzz, Controller_B1.0_doubleExtension.fzz, Controller_B1.0_singleExtension.fzz, Controller_C1.0.fzz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]
2020-12-03 Some modifications to the Controller Firmware
    Name was changed from Controller_A1.0 to Controller_C1.0., but actually the current firmware version is not yet for the actual Controller_C1.0, but for an earlier (not documented) Hardware layout wit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
    [Controller_C1.1.fzz]
2021-03-12 Update after some modifications
    Hard- and Firmware of Controller_X0.1 now work together. The first 8 Valves are fine, two on the other side are problematic. The software now works together with the Firmware of Controller_X. Unfortu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
    Trouble shooting is ongoing.
    Documentation follows as soon as the setup works reliably.
    [Controller_X0.1.fzz, Extension_C1.1.fzz]
2021-04-22 a lot of changes to the software and the firmware, still no officially working stage reached...
    [8x3valveModule_1.0.fzz, Controller_C1.1.fzz, Extension_C1.1.fzz, extension2_1.0.fzz]
2022-05-05 some updates after harddrive crash
    Reinstallation of git desktop after harddrive crash and some time without git...
    [Controller_C1.2.fzz, Extension_C1.1.fzz, Extension_C1.2.fzz, Extension_C1.3..fzz]
2022-05-05 Update Extension_C1.3..fzz
    Jonas Versuch
    [Extension_C1.3..fzz]
2022-05-05 Update Extension_C1.3..fzz
    Geänderter Wiederstand
    [Extension_C1.3..fzz]
2022-05-06 Update Extension_C1.3..fzz
    BagSampler32 Branch
    [Extension_C1.3..fzz]
2022-05-06 smaller changes to Extension_C1.3
    [Extension_C1.3..fzz]
2022-07-15 changes to the controller firmware and the summarizer GUI
    [Bagsampler.fzz, Controller_C1.1.fzz, Extension_C1.3..fzz, Extension_C1.3.fzz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]
2022-09-02 smaller changes
    [Extension_C1.3.fzz, Extension_C1.3_v2.fzz]
2023-01-19 Update Sequencer.py
    Minor change to actually interpret the value of "autoSwitchEnable" in the valve.conf
2023-05-23 some updates
    [Extension_C1.2.fzz, Extra_Extension_C1.2.fzz]
2023-07-17 Some additions to the documentation
    [Extension_C1.2.fzz, WIP_costCalculator.xlsx, WIP_electronicComponents.xlsx]
2024-06-27 Introduced secondary valves
